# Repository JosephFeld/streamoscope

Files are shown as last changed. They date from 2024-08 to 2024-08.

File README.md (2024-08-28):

# Streamoscope
The Streamoscope is a USB-3 data acquisition system designed for low-field MRI, but could be more generally used. It streams two channels at 60 megasamples per second with 14-bit precision and costs around $300 in parts. It can read in data with low latency and the limit of how much can be read is only limited by the RAM on your computer!

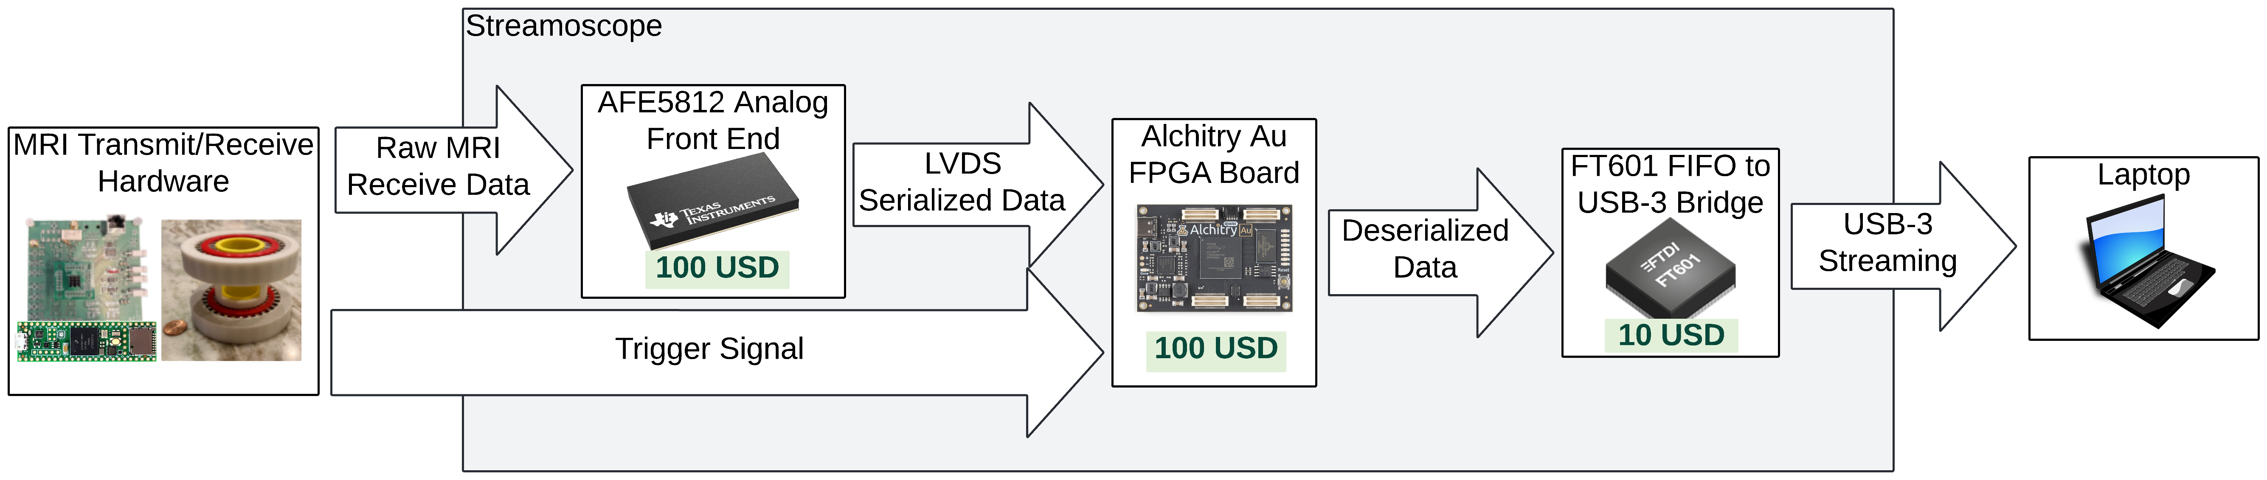
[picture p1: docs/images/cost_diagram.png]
Cost Diagram


It reads in 8 channels of data from the [AFE5812 analog front end chip](https://www.ti.com/product/AFE5812) into an [Alchitry Au FPGA board](https://www.sparkfun.com/products/16527), which feeds it into an [FT601 FIFO-to-USB-3 Bridge](https://ftdichip.com/products/ft601q-b/) which can be read into [Python](https://www.python.org/). Due to bandwidth constraints of the FT601, it only streams two channels. However, more could be streamed with a modified FPGA design that decimates the signals or decreases their precision.

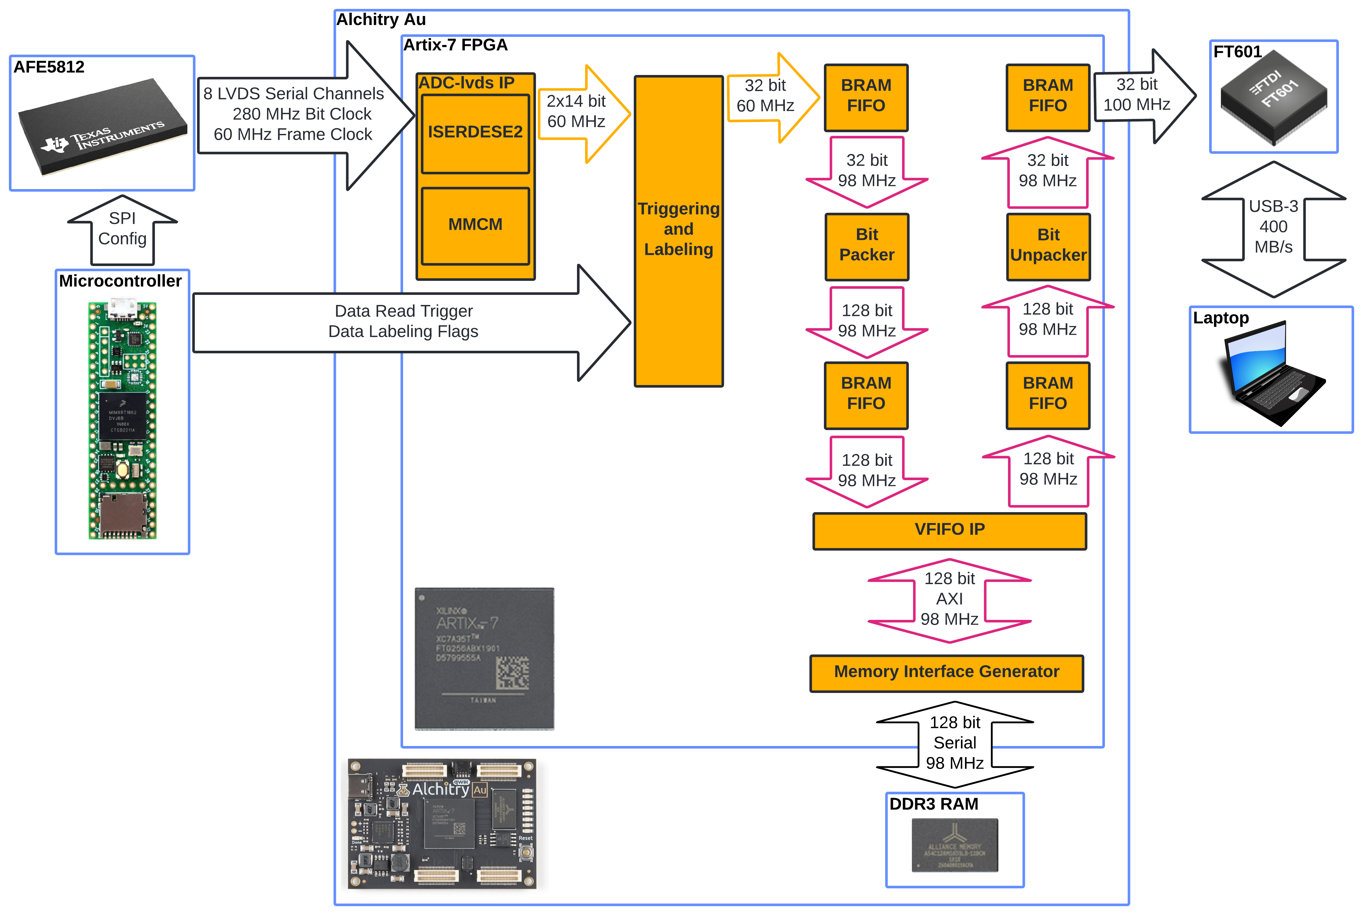
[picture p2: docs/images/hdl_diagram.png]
HDL Diagram


What follows are guides on how to access the various components of the system. To summarize them:

* PCB design files from KiCad
* Python code for reading in data from the FT601
* Teensy code for configuring the AFE5812
* How to configure the Alchitry Au FPGA
* A Vivado project for the FPGA design

# PCB

The PCB design was done in [KiCad 8.0](https://www.kicad.org/) and can be found in ```streamoscope/hardware/kicad_design```. There are custom footprints used, which are accessible in this [library](https://github.com/JosephFeld/Handheld-MRI-Parts). Special thanks to [Lopfi for making the Alchitry Au footprint](https://github.com/Lopfi/alchitry-element-kicad).

# Python Setup

Streamoscope data can be read into Python, and this guide will walk through setting up the Jupyter Notebook example. This uses Python 3, which can be downloaded [here](https://www.python.org/downloads/).

## Installing libusb

First, we need to install [libusb](https://libusb.info/).

### MacOS

On MacOS, run these commands in the terminal: 
```
brew install libusb
sudo ln -s /opt/homebrew/lib/libusb-1.0.0.dylib /usr/local/lib/libusb.dylib
```

### Windows

On Windows, download the latest libusb Windows binaries [here](https://libusb.info/) under Downloads>Latest Windows Binaries.

Unzip the file and choose a version corresponding to your operating system. A good default is the newest Visual Studio folder VS2022. Choose the subfolder corresponding to your operating system, either 32 or 64 for 32-bit or 64-bit systems, respectively. Copy ```libusb-1.0.dll``` in the ```dll``` folder into ```C:/Windows/System32```, which will require admin approval. ```libusb-1.0.dll``` can also be placed into the same directory as the python script, ```streamoscope/software/python_reading``` for this example.

The FT601 on the Streamoscope may have the incorrect drivers. To fix this, install [Zadig](https://zadig.akeo.ie/) and run it.

* Select Options\>List All Devices
* Select FTDI SuperSpeed-FIFO Bridge (Interface 0)
* Use the arrows on the right to select libusbK as the new driver.

Here's what it should look like:
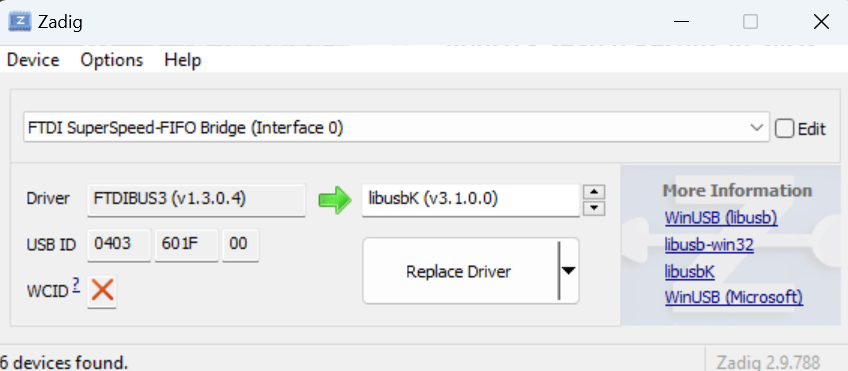
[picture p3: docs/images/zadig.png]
Zadig


* Click "Replace Driver"

## Python dependencies

Then install the Python dependencies

```
pip install libusb, pyusb, matplotlib, numpy, scipy, jupyter
```

## Jupyter Notebook Setup

In the terminal, cd into ```streamoscope/software/python_reading``` and run this command to start up the Jupyter Notebook:

```jupyter notebook .\spin_echo_reader.ipynb```

# Teensy Setup

The Streamoscope uses a Teensy 4.1 microcontroller to configure the AFE5812 Analog Front End and ADC. The software for programming the Teensy can be found [here](https://www.pjrc.com/teensy/td_download.html).

To plug the Teensy into the Streamoscope, connect these pins:

| Streamoscope Pin | Teensy Pin |
| ---------------- | ---------- |
| ADC_RESET        | 3          |      
| MISO             | 39         |
| MOSI             | 26         |
| SCLK             | 27         |
| CS_AFE           | 38         |

And program the Teensy using the code in ```streamoscope\software\teensy_4_1_afe5812_config\teensy_4_1_afe5812_config.ino```. Every time the Teensy powers up, it reconfigures the AFE5812. 

# Configuring Alchitry Au

The Alchitry Au can be programmed using [Alchitry Loader](https://alchitry.com/alchitry-labs/) with the bitstreams found in ```streamoscope/fpga_configurations/```. It is also compatible with [openFPGALoader](https://github.com/trabucayre/openFPGALoader).

There is also a JTAG port broken out which can be used with JTAG programmers like [this](https://digilent.com/shop/jtag-hs3-programming-cable/), which can enable use of the Vivado ILA.

Here are descriptions of each bitstream:

| Filename | Description |
| ---------------- | ---------- |
| teensy_triggered.bit  | Streams channels 1 and 3 with data validity set by GPIO_0 (active high). This is useful for individual spin echoes. |      
| teensy_triggered_with_500ms_trigger_extension.bit | Streams channels 1 and 3 with data validity set by GPIO_0 (active high). Validity lasts an extra 500 milliseconds after GPIO_0 goes low. This is useful for fast imaging sequences. |

# Vivado Project Setup
The FPGA design was made in [Vivado 2023.2](https://www.xilinx.com/support/download/index.html/content/xilinx/en/downloadNav/vivado-design-tools/2023-2.html). It is only necessary to use this if you need to modify the HDL on the FPGA since There is already a provided FPGA configuration.

Open the Vivado GUI, go to the tcl console on the bottom, and cd into the ```streamoscope/hdl/Streamoscope/``` directory. Then run this command:

```
source Streamoscope.tcl
```

Then wait for a bit while the project configures. It will open up the new Streamoscope project. Then in the new project's tcl console, generate the modified ADC LVDS IP with these commands:

```
cd ../ADC-lvds-main/ip
source adc_lvds_ip.tcl
```

Then run this command in the Streamoscope tcl console to update the IP catalog:

```
update_ip_catalog -rebuild
```

If you're running on a version after 2023.2, you may need to update the IP versions. You can do that by navigating to Reports>Report IP Status. In the menu that pops up, select Upgrade Selected.

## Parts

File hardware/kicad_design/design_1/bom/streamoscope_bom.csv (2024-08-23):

Id | Designator | Footprint | Quantity | Designation | Supplier and ref | supplemental parts
1 | J7 | PinHeader_1x32_P2.54mm_Vertical | 1 | Conn_01x32_Pin | https://www.mouser.com/ProductDetail/TE-Connectivity/3-826936-2?qs=xF5SkmKSM76zfahaczRa9A%3D%3D
2 | F1 | Fuse_0402_1005Metric_Pad0.77x0.64mm_HandSolder | 1 | Fuse | https://www.mouser.com/ProductDetail/Littelfuse/043502.5KRHF?qs=PalBzRKzfnviFVYPMWoZ5g%3D%3D
3 | J16 | PinHeader_1x16_P2.54mm_Vertical | 1 | Conn_01x16_Pin | https://www.mouser.com/ProductDetail/Amphenol-FCI/68024-116HLF?qs=C9AXj6SgtYUh%2FNWF9cqh4A%3D%3D | https://www.mouser.com/ProductDetail/Samtec/IDSS-16-D-20.00?qs=rU5fayqh%252BE0O0Dd9%252BPEI9Q%3D%3D
4 | J15 | AMPHENOL_12401899E412A | 1 | USB_C_Receptacle | https://www.mouser.com/ProductDetail/Amphenol-Commercial-Products/12401899E412A?qs=0lSvoLzn4L%2FxruERFi%2FtTg%3D%3D
5 | C33,C31,C17,C16,C42,C29,C30,C44,C32,C55,C43 | C_0402_1005Metric_Pad0.74x0.62mm_HandSolder | 11 | 1u | https://www.mouser.com/ProductDetail/KYOCERA-AVX/KGM05AR51A105KH
6 | R7,R8,R10,R15 | R_0402_1005Metric_Pad0.72x0.64mm_HandSolder | 4 | 10k | https://www.mouser.com/ProductDetail/TE-Connectivity-Holsworthy/RN73C1E10KBTD?qs=CXI0wBT1M2iAWhqqLC6L1g%3D%3D
7 | C9,C35,C10,C11,C34,C12,C5,C13 | C_0402_1005Metric_Pad0.74x0.62mm_HandSolder | 8 | 15n | https://www.mouser.com/ProductDetail/KEMET/C0402C153K3RACTU?qs=ZP3UR5XsUoduxSHfolMWsA%3D%3D
8 | C38,C15,C47,C53,C20,C23,C78,C3,C40,C50,C58,C19,C41,C26,C45,C51,C79,C46,C27,C14,C39,C36,C77,C28,C24,C25,C57,C22,C4,C48,C21,C49,C18,C37,C56 | C_0402_1005Metric_Pad0.74x0.62mm_HandSolder | 35 | 0.1u | https://www.mouser.com/ProductDetail/KYOCERA-AVX/0402X7R104KT7AT
9 | J1 | PinHeader_1x02_P2.54mm_Vertical | 1 | Conn_01x02_Pin
10 | C7,C2,C8,C1 | CP_EIA-6032-20_AVX-F | 4 | 22u | https://www.mouser.com/ProductDetail/KYOCERA-AVX/TPSC226K016R0375?qs=iBwFsHVUAOd%252BY4clhItAJQ%3D%3D
11 | FB3,FB7,FB5,FB9,FB8,FB6,FB2,FB4 | L_0805_2012Metric | 8 | FerriteBead | https://www.mouser.com/ProductDetail/Laird-Performance-Materials/HI0805R800R-10?qs=UV0HhPl4yOF%252BhNGXb8sElA%3D%3D
12 | J11,J8,J13,J6,J10,J9,J5,J12 | SMA_Amphenol_132134_Vertical | 8 | Conn_Coaxial | https://www.mouser.com/ProductDetail/LPRS/SMA-CONNECTOR?qs=j%252B1pi9TdxUYkOiITvzJM8A%3D%3D
13 | FB11 | L_0402_1005Metric | 1 | FerriteBead | https://www.mouser.com/ProductDetail/Murata-Electronics/BLM15BD102SN1D?qs=VC7md5PxyA1Y4EgP9YhX%252BA%3D%3D
14 | C59,C61,C72,C54,C62,C63,C68,C66,C67 | C_0402_1005Metric_Pad0.74x0.62mm_HandSolder | 9 | 100n | https://www.mouser.com/ProductDetail/KYOCERA-AVX/0402X7R104KT7AT
15 | JPG1,JPG2 | R_0402_1005Metric_Pad0.72x0.64mm_HandSolder | 2 | 0 | https://www.mouser.com/ProductDetail/Vishay-Dale/CRCW04020000Z0EDC?qs=sGAEpiMZZMtlubZbdhIBIIZe04wfiaJW9KIkhfRMZVI%3D
16 | C73,C70,C71,C69,C65,C64 | C_0402_1005Metric_Pad0.74x0.62mm_HandSolder | 6 | 470n | https://www.mouser.com/ProductDetail/KYOCERA-AVX/0402ZC474KAT2A
17 | R1 | R_0402_1005Metric_Pad0.72x0.64mm_HandSolder | 1 | 49.9 | https://www.mouser.com/ProductDetail/Panasonic/ERA-2AED49R9X?qs=sGAEpiMZZMtlubZbdhIBIKHZJwodQ036pHeX4trellw%3D
18 | D2,D1 | LED_0603_1608Metric | 2 | Green | https://www.mouser.com/ProductDetail/ROHM-Semiconductor/SMLD12EN1WT86?qs=qSfuJ%252Bfl%2Fd4fR%252B9yZydIwg%3D%3D
19 | R3,R2 | R_0402_1005Metric_Pad0.72x0.64mm_HandSolder | 2 | 200 | https://www.mouser.com/ProductDetail/Vishay-Dale/CRCW0402200RFKEDHP?qs=sGAEpiMZZMtlubZbdhIBIHEwn6Ulz00PjH77PBDsIyo%3D
20 | X1 | Oscillator_SMD_Abracon_ASV-4Pin_7.0x5.1mm | 1 | XO32 | https://www.mouser.com/ProductDetail/ABRACON/ASV-60.000MHZ-E-T?qs=NE97hfUNX0FMmM33%252BKetqA%3D%3D&countryCode=US&currencyCode=USD
21 | U1 | IC_TPS61196PWPRQ1 | 1 | TPS767D318PWPR | https://www.mouser.com/ProductDetail/Texas-Instruments/TPS767D318PWPR?qs=6zVL%252ByCp0mo1sIrGyoyUVQ%3D%3D
22 | J14 | BarrelJack_Horizontal | 1 | Barrel_Jack | https://www.mouser.com/ProductDetail/Wurth-Elektronik/694106301002?qs=a9WhcLg8qCwOEkcI62k5mA%3D%3D | alt: | https://www.digikey.com/en/products/detail/cui-devices/PJ-002AH/408446
23 | IC1 | SOT95P280X130-5N | 1 | MIC7221YM5-TR | https://www.mouser.com/ProductDetail/Microchip-Technology/MIC7221YM5-TR?qs=U6T8BxXiZAWrxxu6IxkTvA%3D%3D
24 | C52,C60 | C_0402_1005Metric_Pad0.74x0.62mm_HandSolder | 2 | 6.8n | https://www.mouser.com/ProductDetail/KYOCERA-AVX/04025C682K4T2A
25 | U2 | QFN40P900X900X100-77N | 1 | FT601Q-B-T | https://www.mouser.com/ProductDetail/FTDI/FT601Q-B-T?qs=p9T7GgSe1IHuZCV7KGuelQ%3D%3D
26 | U4 | ZCF135_TEX_NO_PASTE | 1 | AFE5812ZCF | https://www.mouser.com/ProductDetail/Texas-Instruments/AFE5812ZCF?qs=jpHf3Ogds1wdWEifNjYuZA%3D%3D
27 | R4,R5 | R_0402_1005Metric_Pad0.72x0.64mm_HandSolder | 2 | 250K | https://www.mouser.com/ProductDetail/Panasonic/ERJ-PA2D2493X?qs=sGAEpiMZZMtlubZbdhIBIA9n2NI7aX0AgwM9v08p8RI%3D
28 | R12,R6 | R_0402_1005Metric_Pad0.72x0.64mm_HandSolder | 2 | 5.1k | https://www.mouser.com/ProductDetail/Vishay-Dale/CRCW04025K10JNED
29 | J3 | PinSocket_2x07_P2.00mm_Vertical | 1 | Conn_02x07_Odd_Even | https://www.mouser.com/ProductDetail/Molex/87831-1435?qs=kNSQ05%252BLZoDWRPEqPkM6DQ%3D%3D
30 | R16,R14 | R_0402_1005Metric_Pad0.72x0.64mm_HandSolder | 2 | 100k | https://www.mouser.com/ProductDetail/Panasonic/ERJ-H2RD1003X?qs=eP2BKZSCXI4AgmLrPoTcjA%3D%3D
31 | U3 | SN74HCS541RKSR | 1 | HD3SS3212IRKSR | https://www.mouser.com/ProductDetail/Texas-Instruments/HD3SS3212IRKSR?qs=GURawfaeGuCBk5SYUlUAfw%3D%3D
32 | C75,C74 | C_0402_1005Metric_Pad0.74x0.62mm_HandSolder | 2 | 18p | https://www.mouser.com/ProductDetail/KYOCERA-AVX/04025A180GAT2A?qs=tGdZP2ZdRP0kqZUhomJhdQ%3D%3D
33 | C6 | C_0402_1005Metric_Pad0.74x0.62mm_HandSolder | 1 | 0.1u | https://www.mouser.com/ProductDetail/KYOCERA-AVX/0402X7R104KT7AT
34 | C76 | C_0402_1005Metric_Pad0.74x0.62mm_HandSolder | 1 | 10u | https://www.mouser.com/ProductDetail/KYOCERA-AVX/04024D106MAT2A?qs=NBFAU1oqP4W0zKsr62mI7A%3D%3D
35 | R9,R13 | R_0402_1005Metric_Pad0.72x0.64mm_HandSolder | 2 | 4.3k | https://www.mouser.com/ProductDetail/Vishay-Dale/CRCW04024K30JNED?qs=hAuyw6LW%252BLgIGQh4eckejg%3D%3D
36 | R11 | R_0402_1005Metric_Pad0.72x0.64mm_HandSolder | 1 | 1.6k | https://www.mouser.com/ProductDetail/Vishay-Dale/CRCW04021K60FKTD?qs=8YOjkUvjcV0g3cR%252BZ1c%2FJA%3D%3D
37 | Y1 | Crystal_SMD_3225-4Pin_3.2x2.5mm | 1 | 30Meg | https://www.mouser.com/ProductDetail/Wurth-Elektronik/830059646?qs=2WXlatMagcF%252BLmGDoXCbKA%3D%3D
38 | J4 | PinSocket_1x04_P2.54mm_Vertical | 1 | Conn_01x04_Pin | https://www.mouser.com/ProductDetail/Amphenol-FCI/68000-204HLF?qs=osVJq4lsVJeuKNYS29q3NQ%3D%3D
39 | B1 | Element_no_top | 1 | Alchitry_Element_AU | https://www.mouser.com/ProductDetail/SparkFun/DEV-16527?qs=W%2FMpXkg%252BdQ6G3CPW%2FClVVA%3D%3D
40 | TP3 | TestPoint_Pad_2.0x2.0mm | 1 | 3.3VA
41 | TP6 | TestPoint_Pad_2.0x2.0mm | 1 | 1.8VD
42 | TP7 | TestPoint_Pad_2.0x2.0mm | 1 | GND
43 | TP4 | TestPoint_Pad_2.0x2.0mm | 1 | 3.3VD
44 | TP5 | TestPoint_Pad_2.0x2.0mm | 1 | 1.8VA
45 | TP1 | TestPoint_Pad_2.0x2.0mm | 1 | 5VA
46 | TP2 | TestPoint_Pad_2.0x2.0mm | 1 | 5V

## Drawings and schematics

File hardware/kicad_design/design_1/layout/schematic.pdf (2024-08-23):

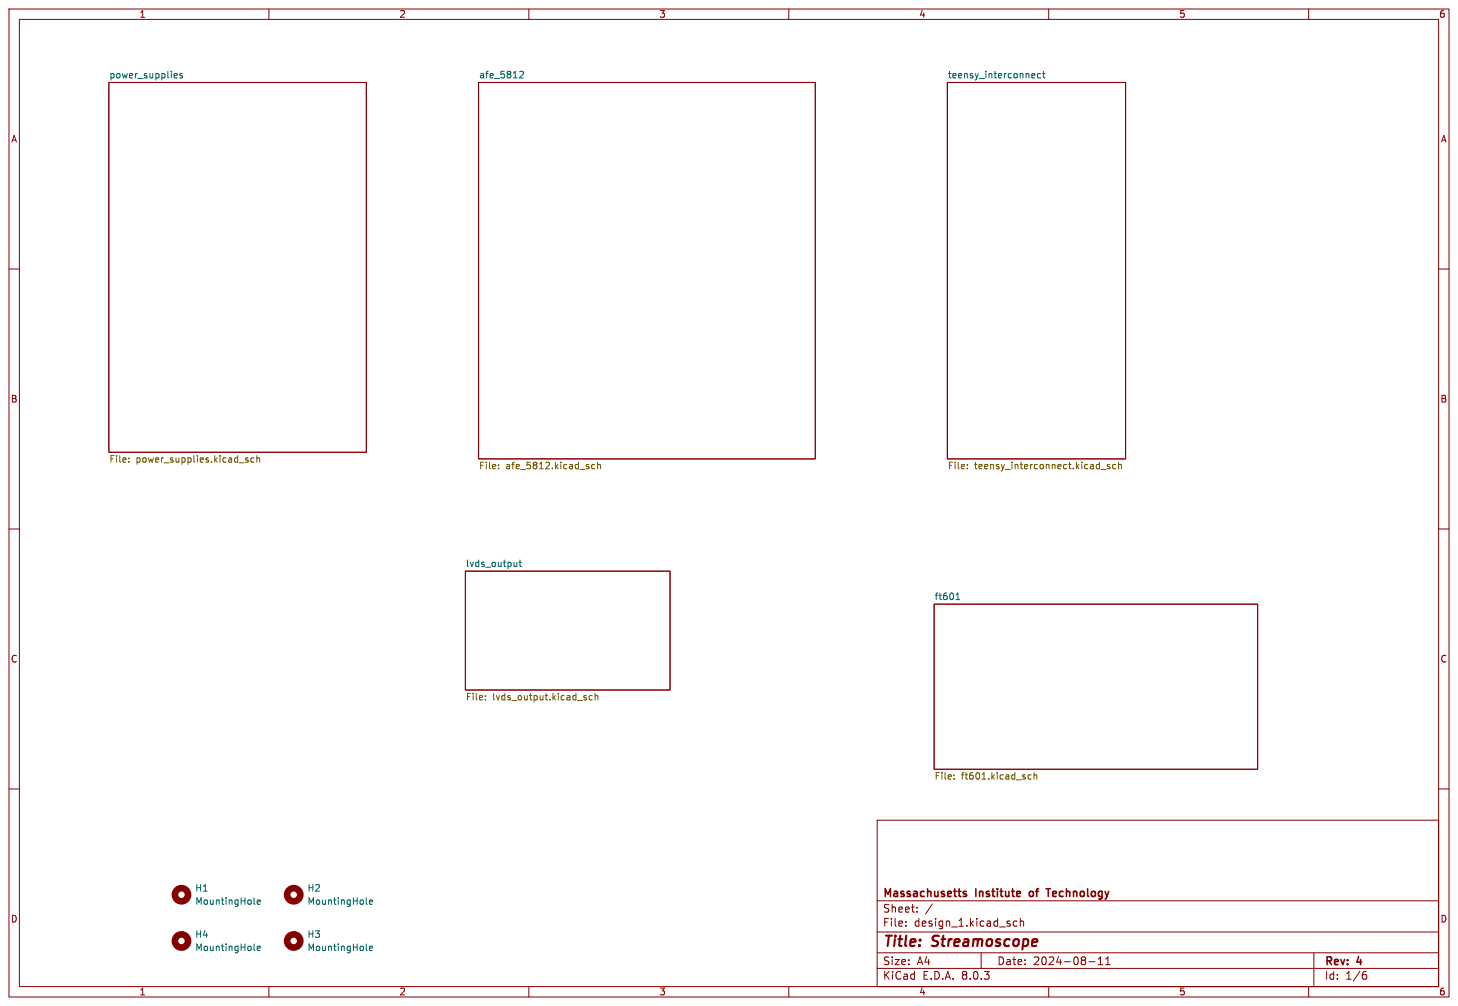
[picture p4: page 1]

ft601 File: ft601.kicad_sch H3 MountingHole H2 MountingHole H4 MountingHole H1 MountingHole

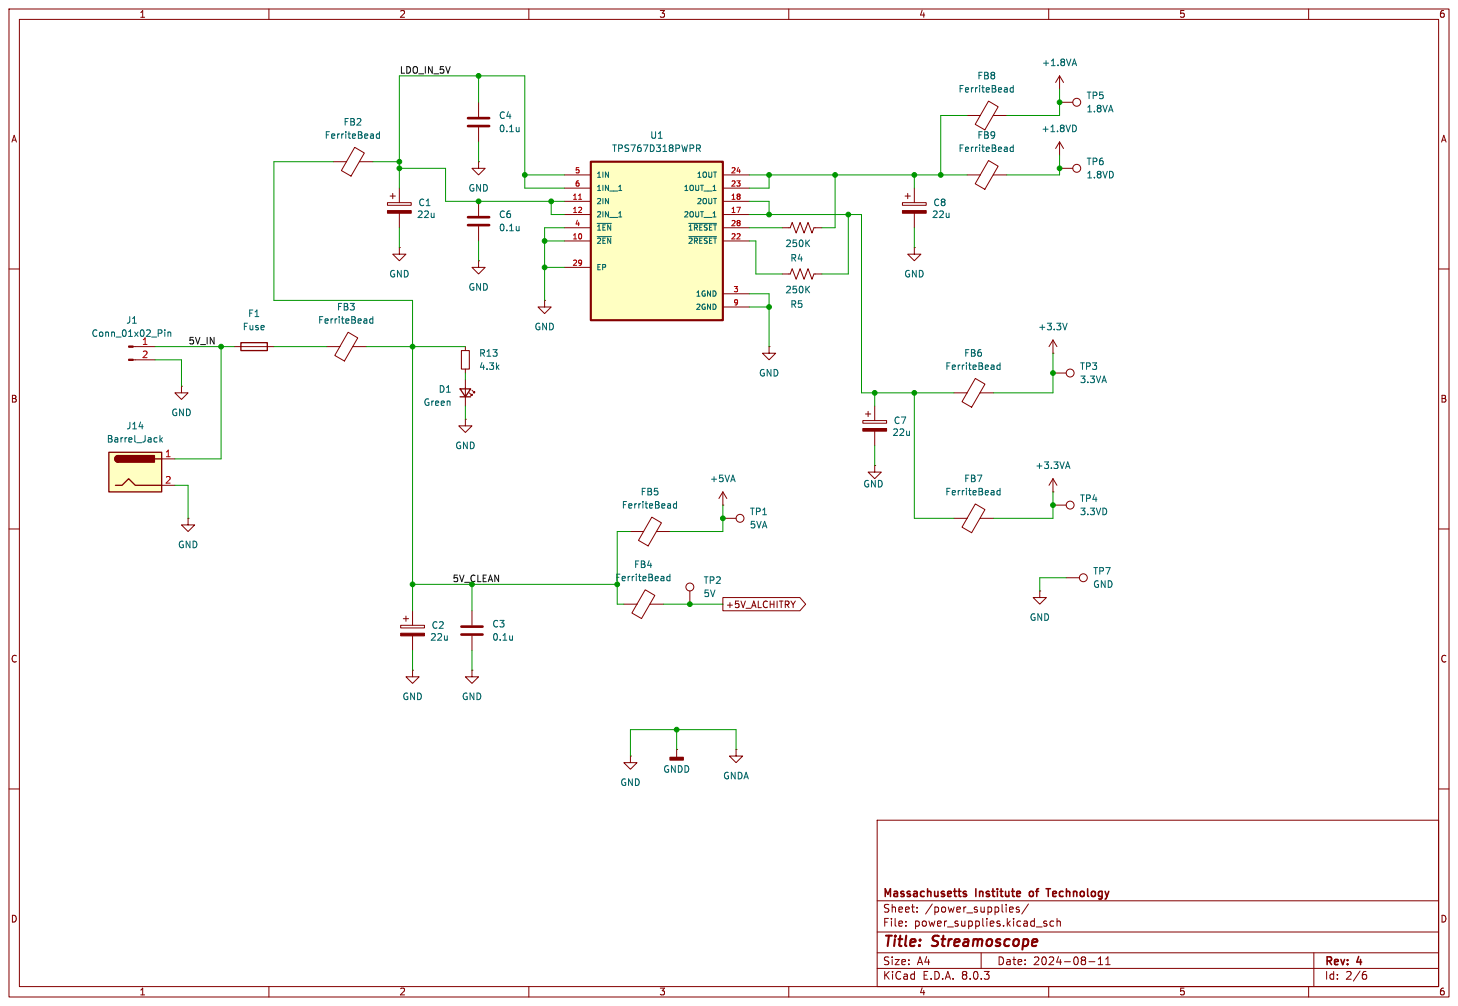
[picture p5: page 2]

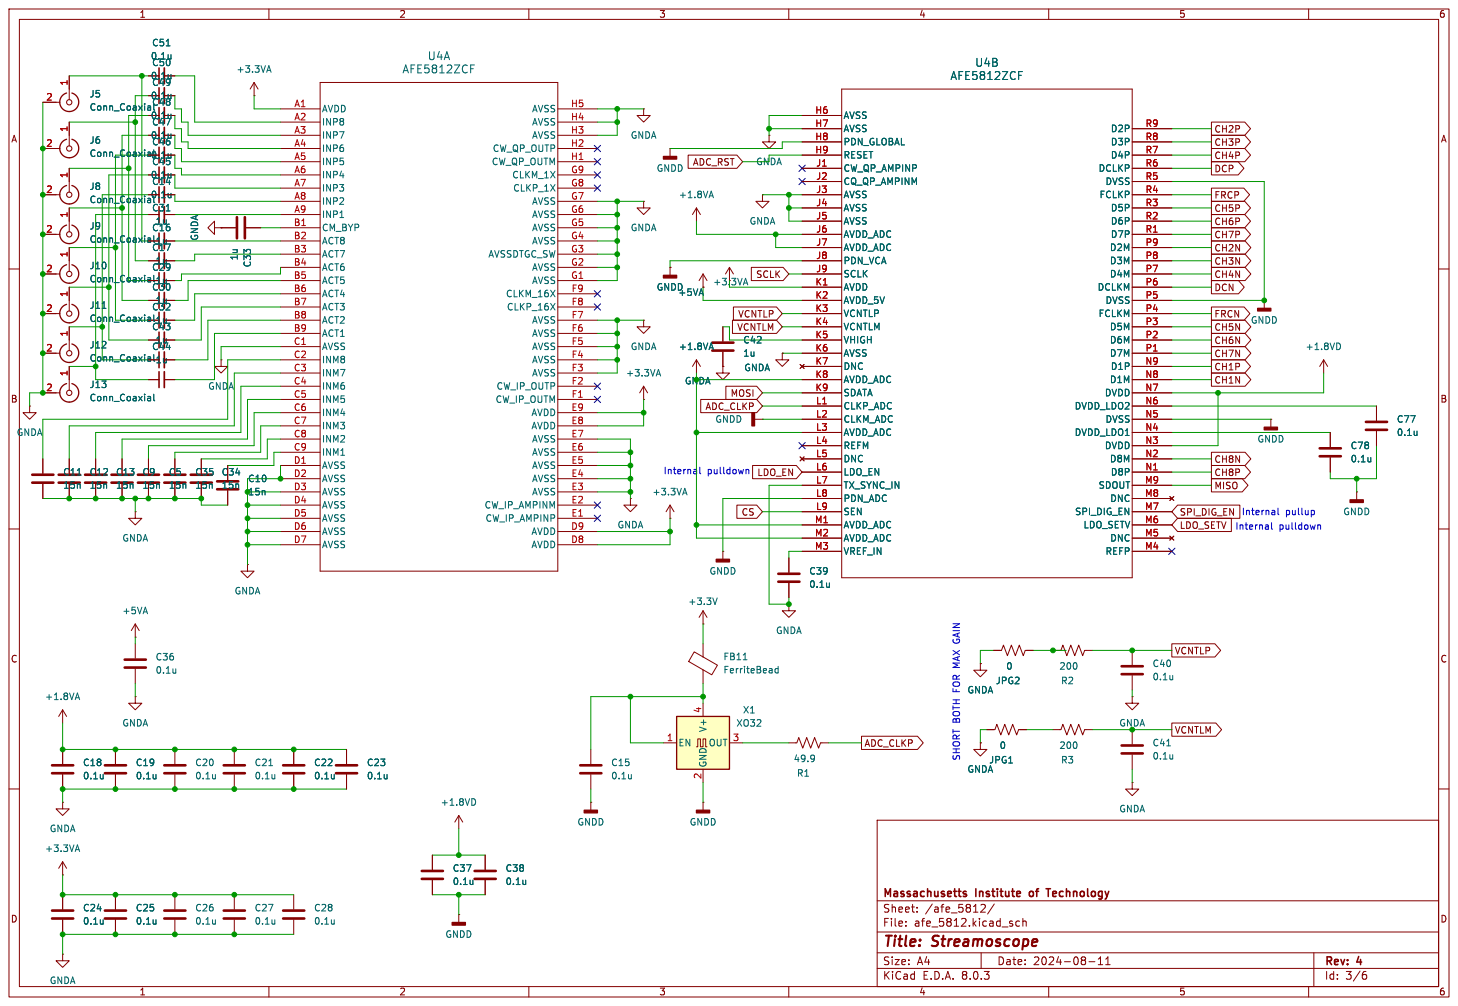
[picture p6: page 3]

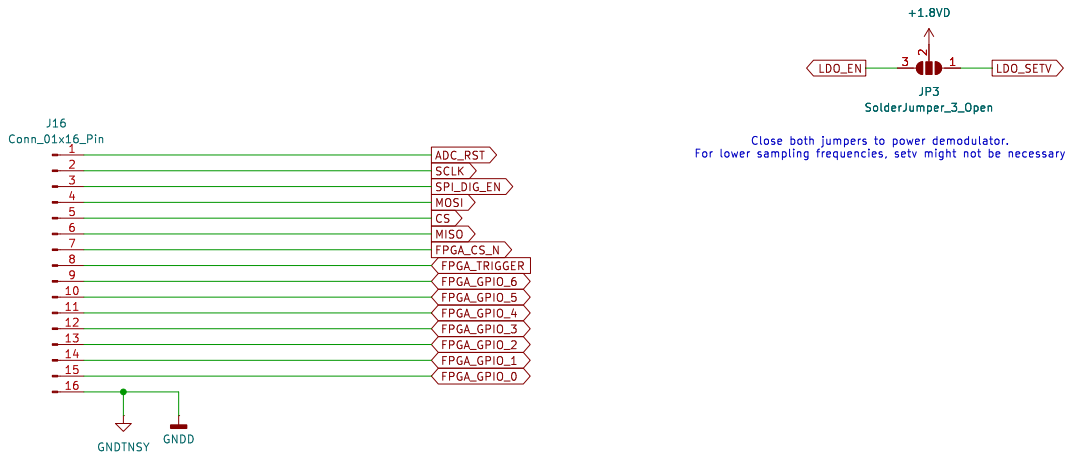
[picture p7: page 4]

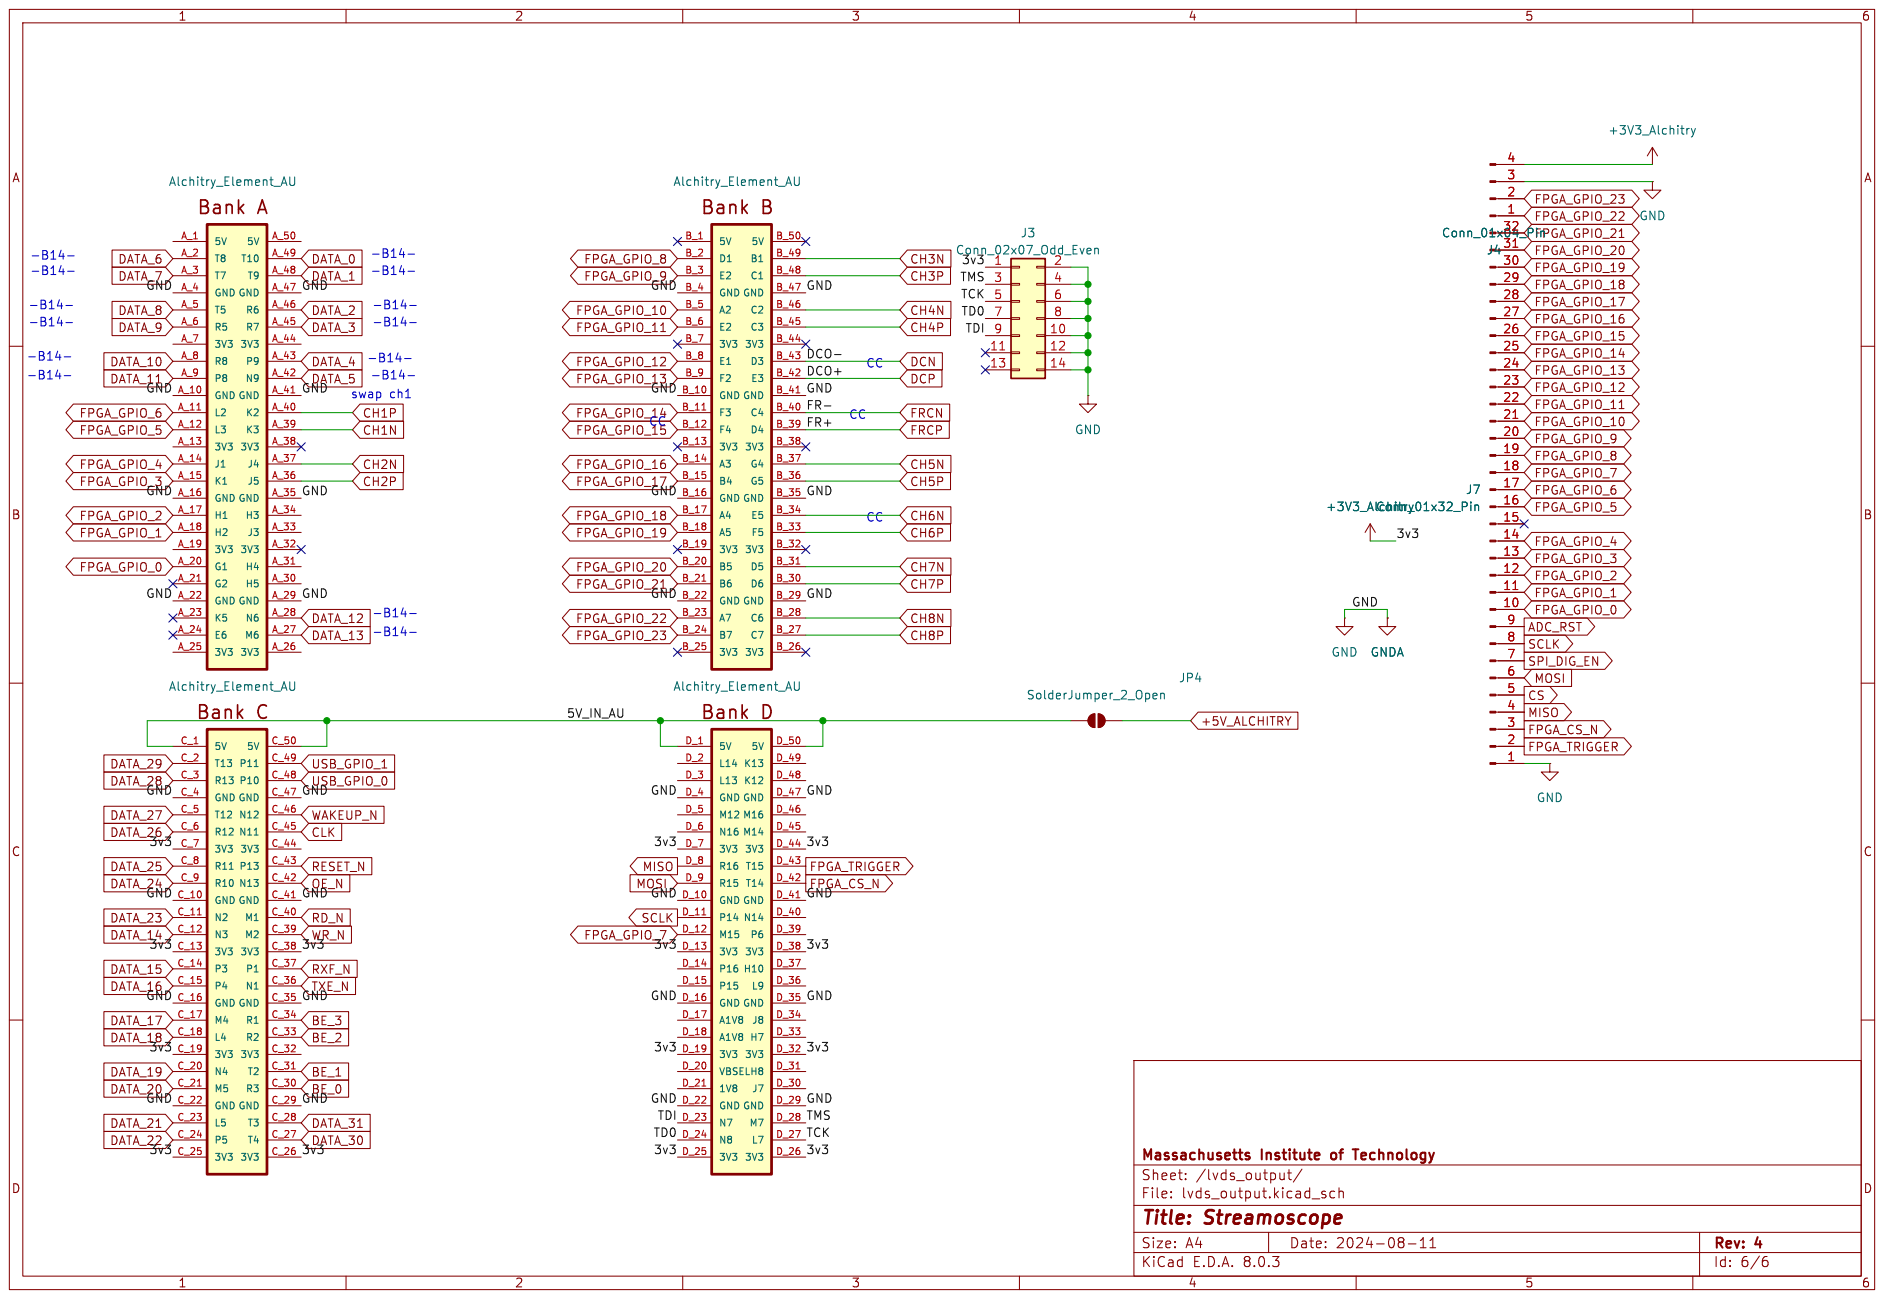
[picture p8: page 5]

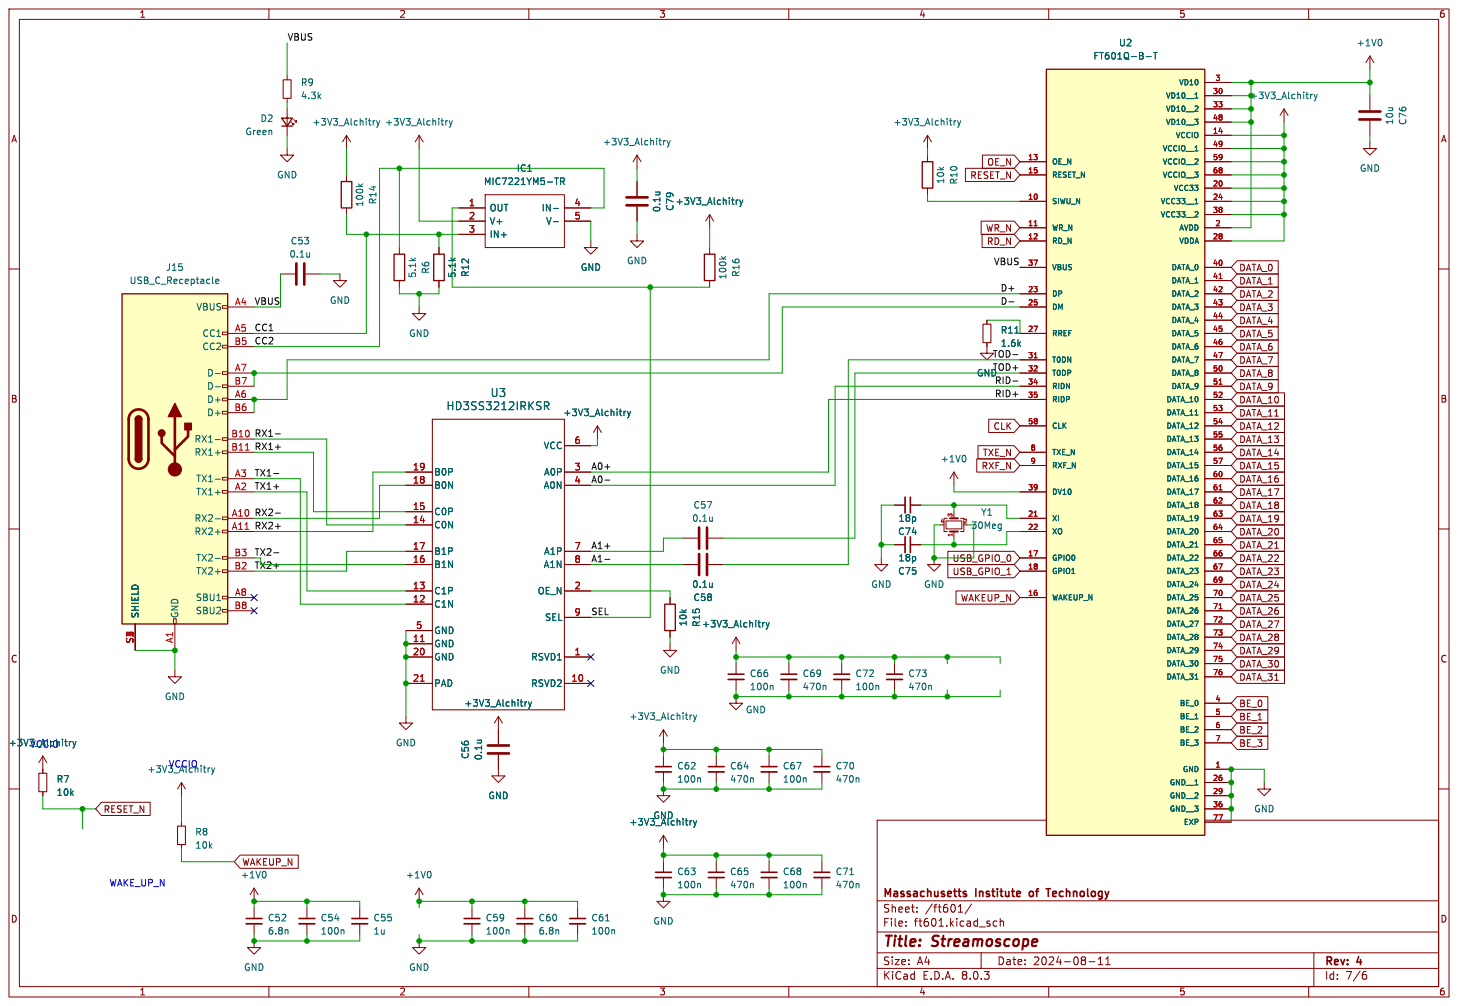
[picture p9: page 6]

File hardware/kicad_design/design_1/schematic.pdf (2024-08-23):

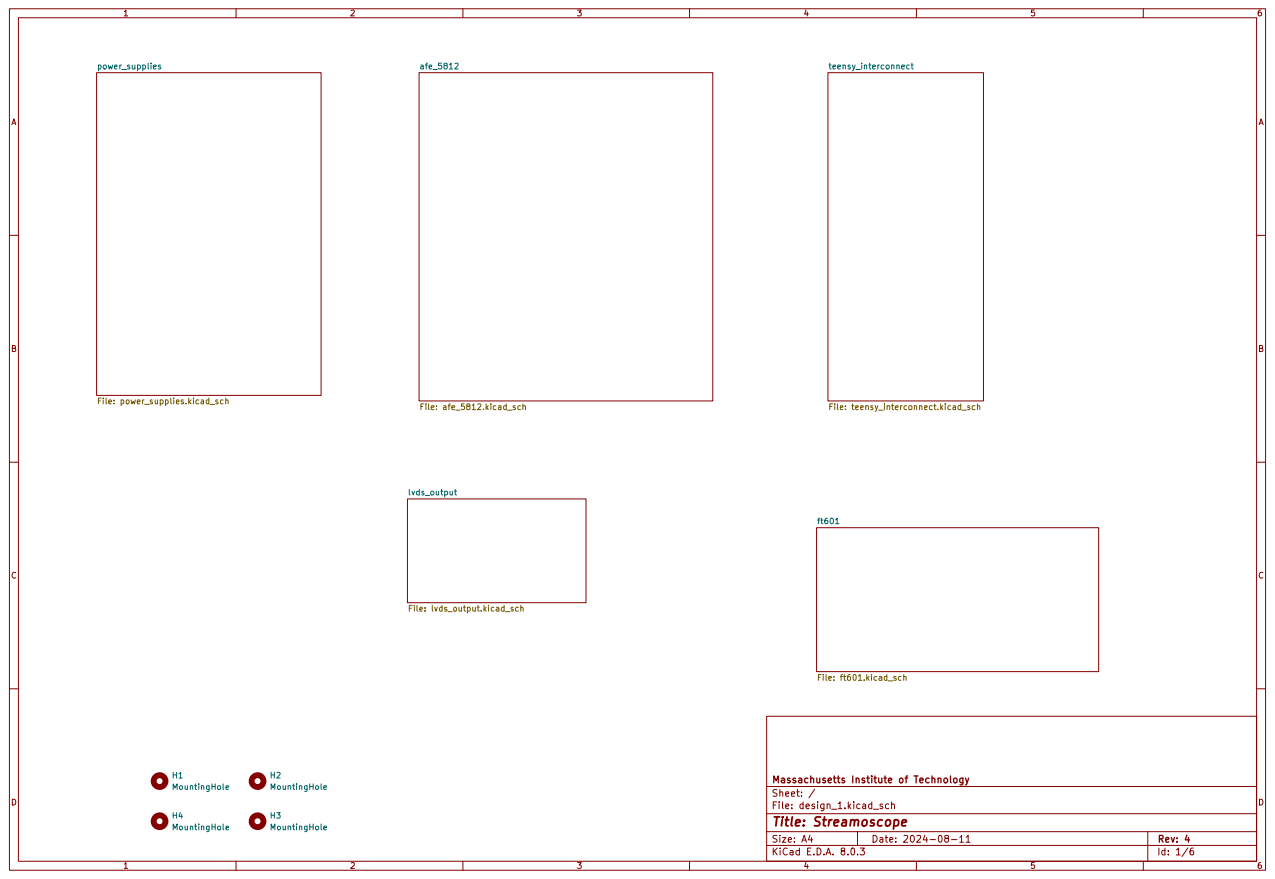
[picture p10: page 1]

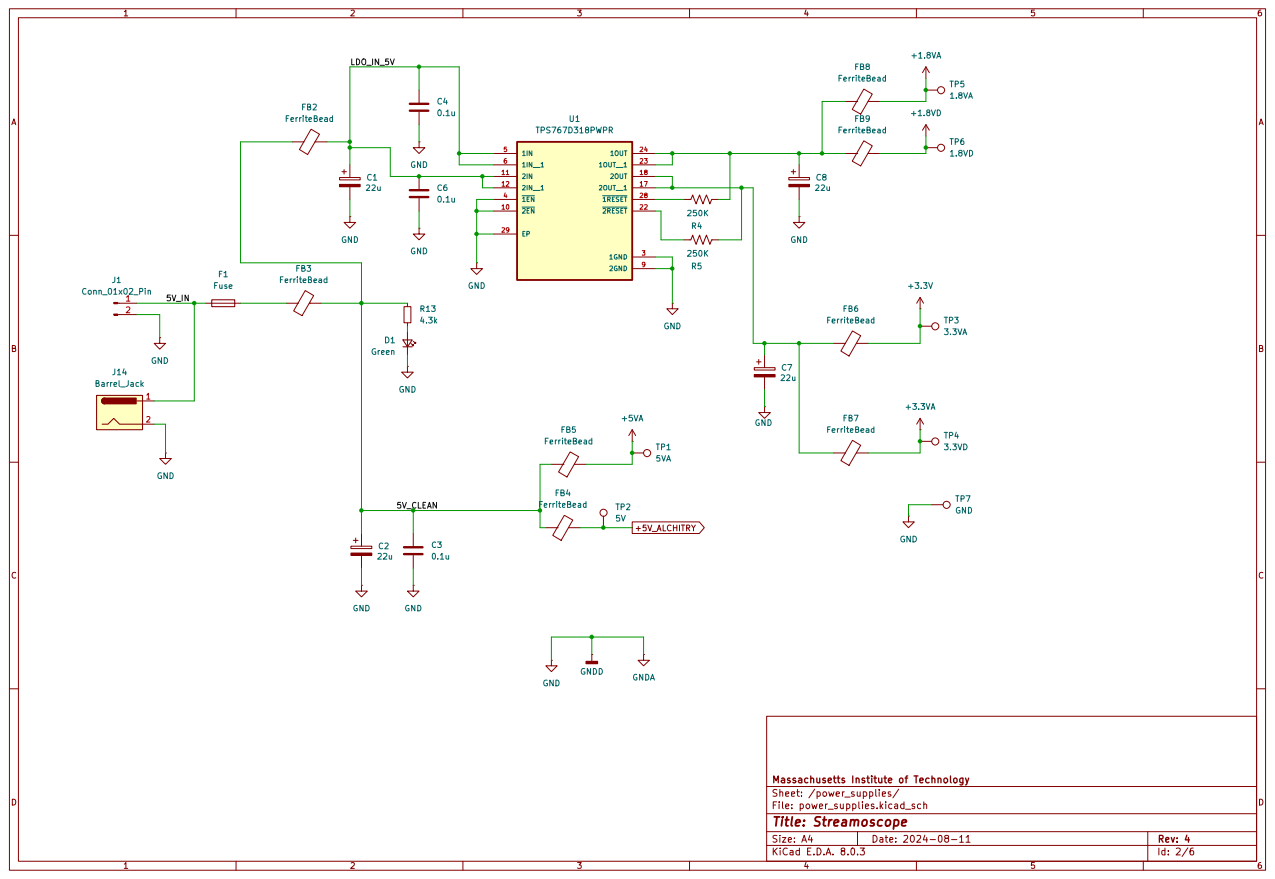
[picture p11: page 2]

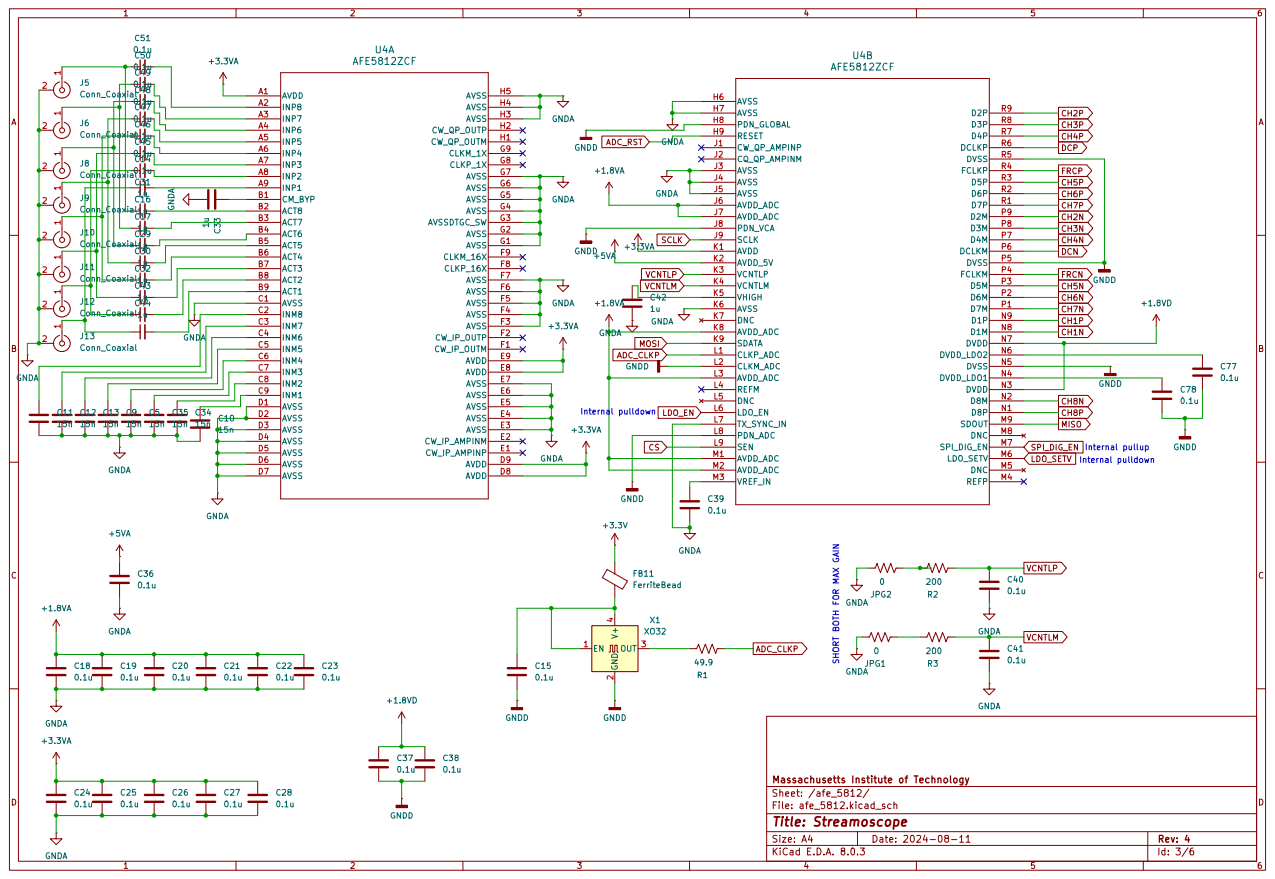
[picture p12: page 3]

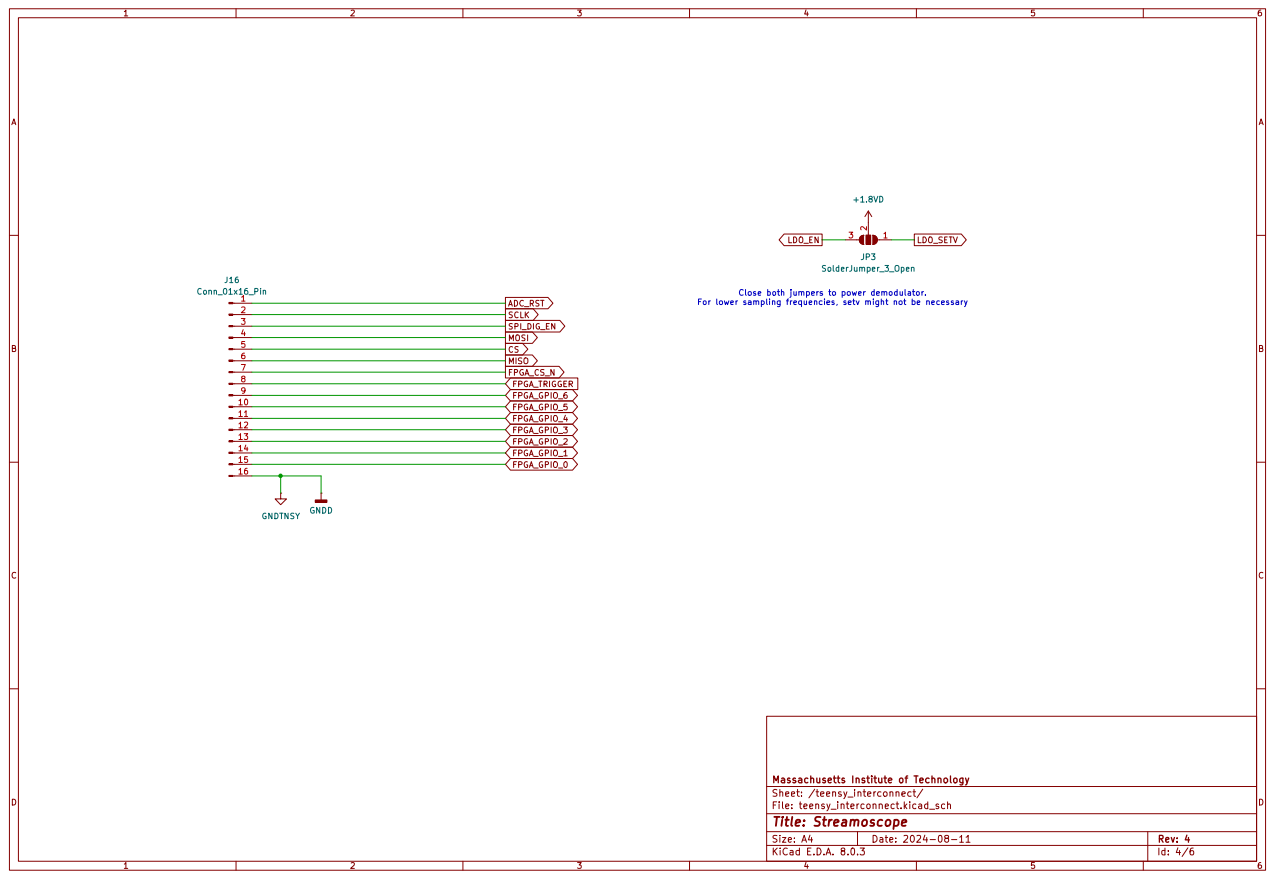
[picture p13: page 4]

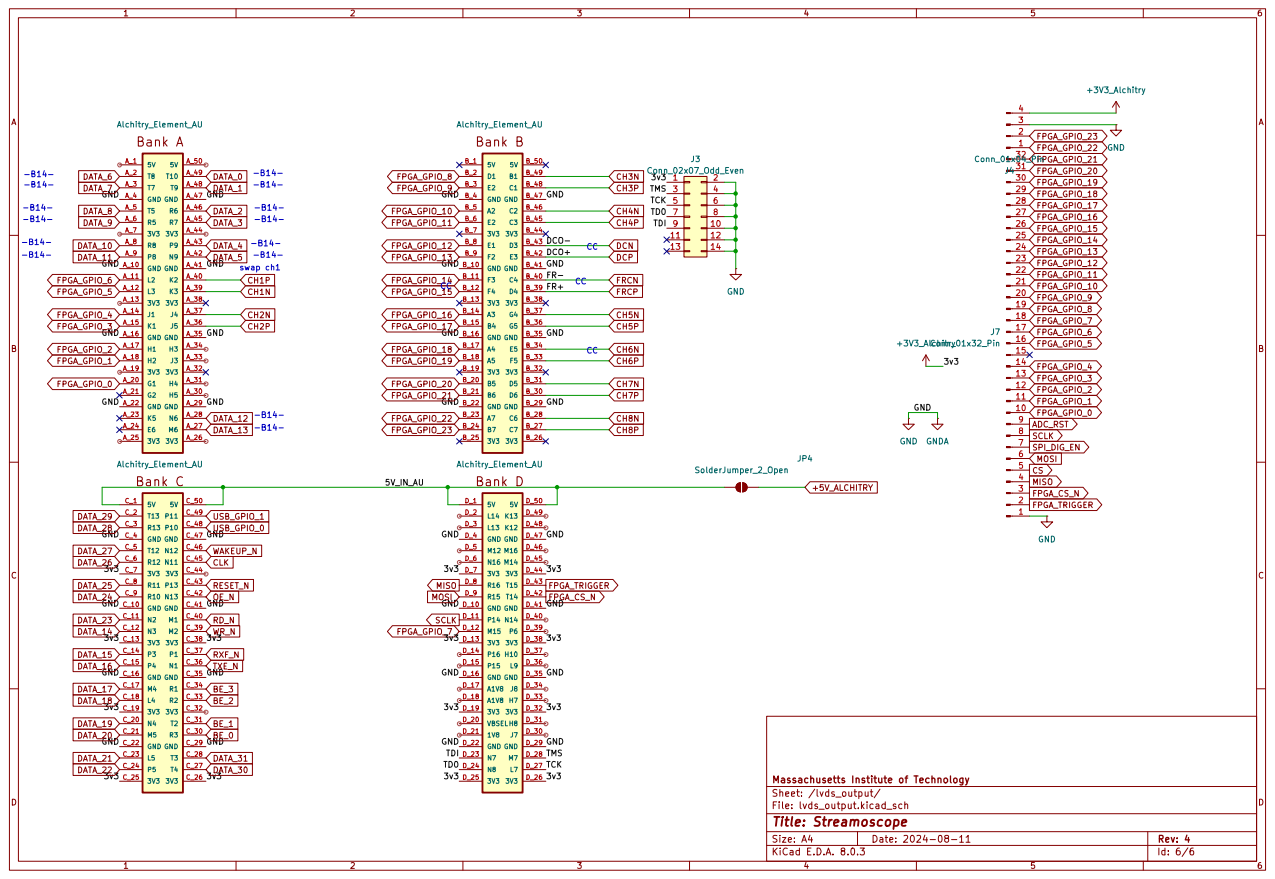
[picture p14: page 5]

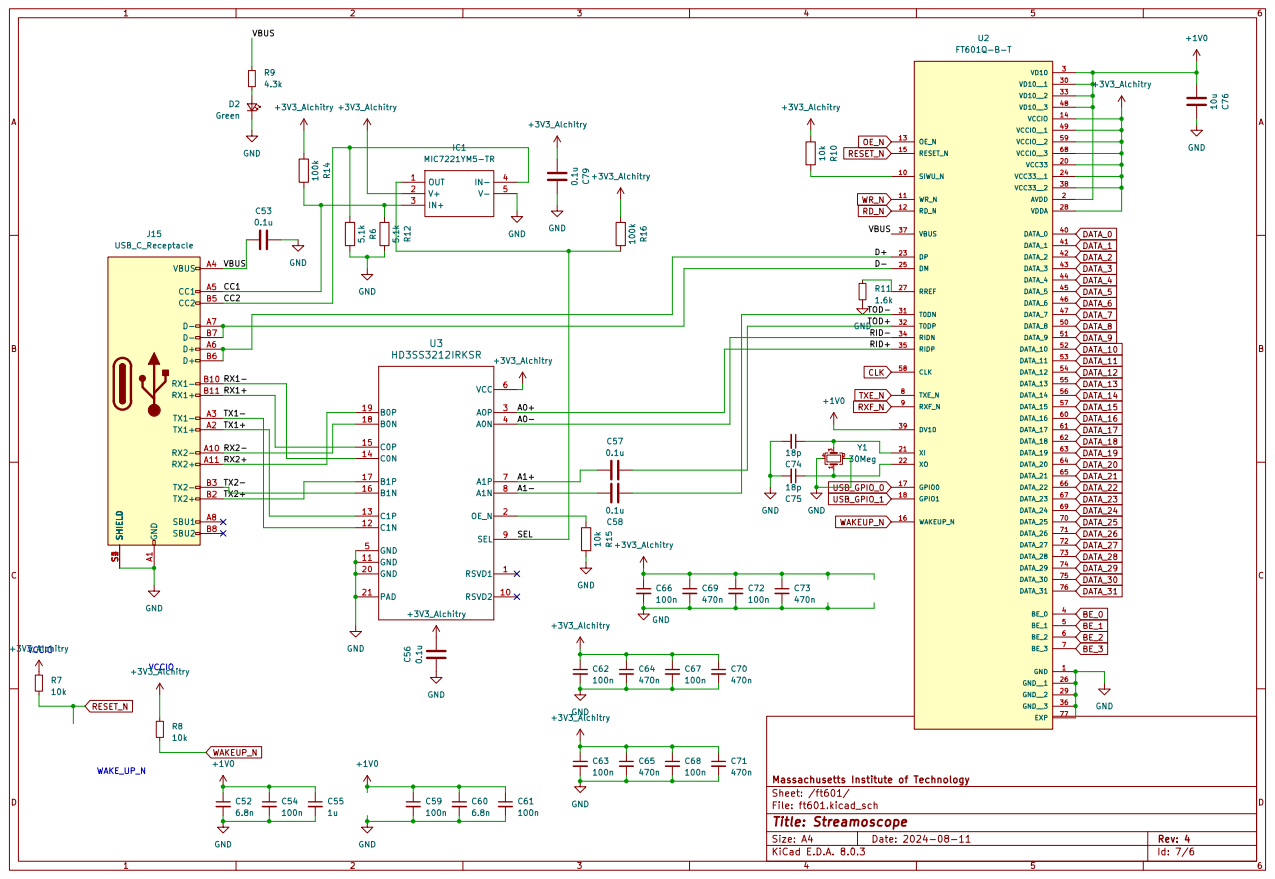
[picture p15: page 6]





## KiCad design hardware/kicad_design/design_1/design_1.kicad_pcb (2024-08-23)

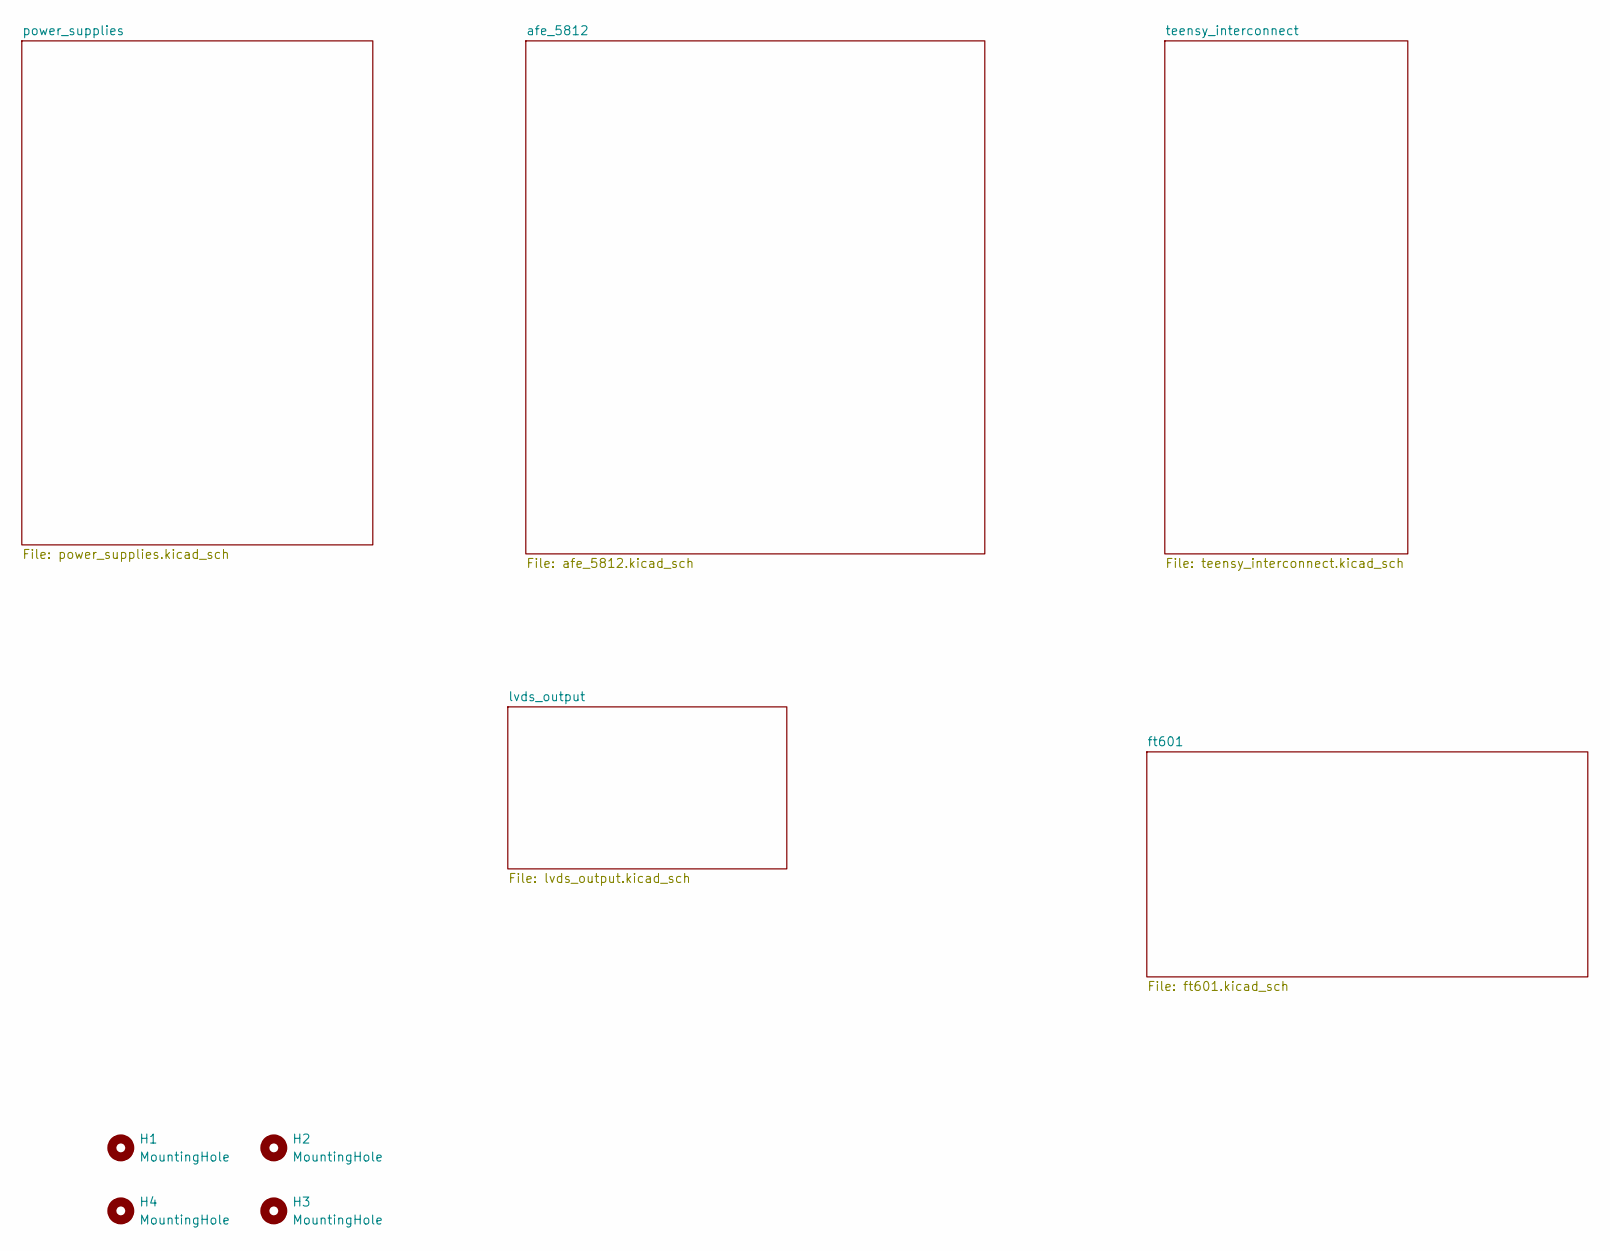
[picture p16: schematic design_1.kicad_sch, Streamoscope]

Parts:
H1, H2, H3, H4: MountingHole; MountingHole_2.2mm_M2

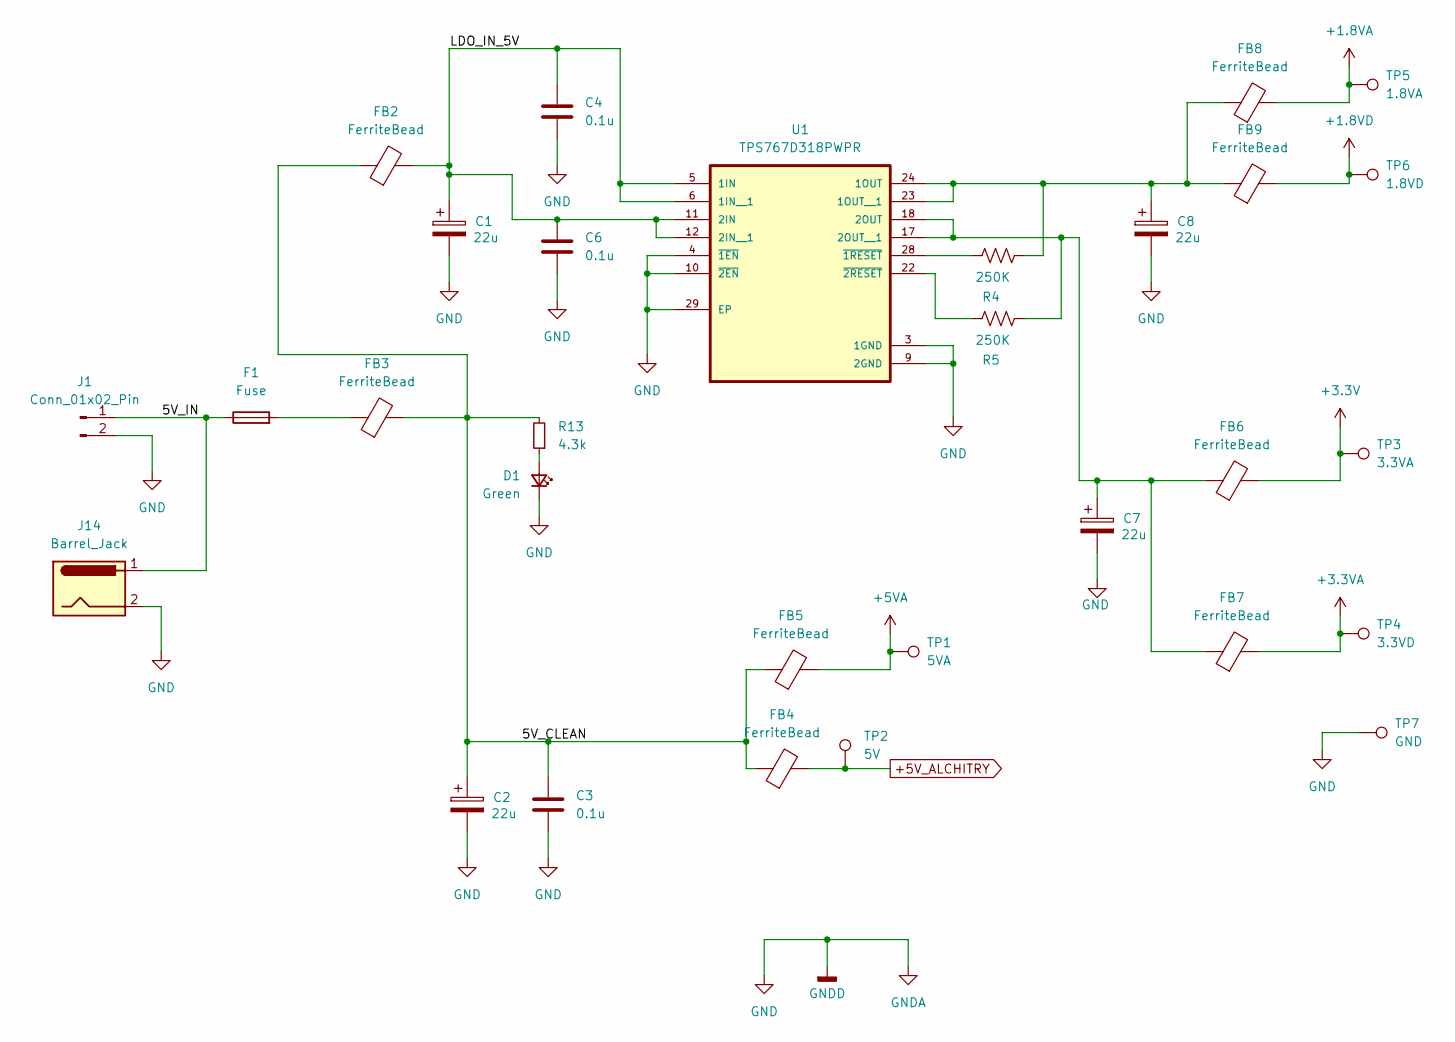
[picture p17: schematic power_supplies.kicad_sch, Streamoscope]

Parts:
C1, C2, C7, C8: 22u; CP_EIA-6032-20_AVX-F
C3, C4, C6: 0.1u; C_0402_1005Metric_Pad0.74x0.62mm_HandSolder
D1: Green; LED_0603_1608Metric
F1: Fuse; Fuse_0402_1005Metric_Pad0.77x0.64mm_HandSolder
FB2, FB3, FB4, FB5, FB6, FB7, FB8, FB9: FerriteBead; L_0805_2012Metric
J1: Conn_01x02_Pin; PinHeader_1x02_P2.54mm_Vertical
J14: Barrel_Jack; BarrelJack_Horizontal
R4, R5: 250K; R_0402_1005Metric_Pad0.72x0.64mm_HandSolder
R13: 4.3k; R_0402_1005Metric_Pad0.72x0.64mm_HandSolder
TP1: 5VA; TestPoint_Pad_2.0x2.0mm
TP2: 5V; TestPoint_Pad_2.0x2.0mm
TP3: 3.3VA; TestPoint_Pad_2.0x2.0mm
TP4: 3.3VD; TestPoint_Pad_2.0x2.0mm
TP5: 1.8VA; TestPoint_Pad_2.0x2.0mm
TP6: 1.8VD; TestPoint_Pad_2.0x2.0mm
TP7: GND; TestPoint_Pad_2.0x2.0mm
U1: TPS767D318PWPR; IC_TPS61196PWPRQ1

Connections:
+1.8VA: FB8.2, TP5.1; also elsewhere on the board
+1.8VD: FB9.2, TP6.1; also elsewhere on the board
+3.3V: FB6.2, TP3.1; also elsewhere on the board
+3.3VA: FB7.2, TP4.1; also elsewhere on the board
+5VA: FB5.2, TP1.1; also elsewhere on the board
+5V_ALCHITRY: FB4.2, TP2.1; also elsewhere on the board
/power_supplies/5V_CLEAN: C2.1, C3.1, FB2.1, FB3.2, FB4.1, FB5.1, R13.2
/power_supplies/5V_IN: F1.1, J1.1, J14.1
/power_supplies/LDO_IN_5V: C1.1, C4.1, C6.1, FB2.2, U1.5 (1IN), U1.6 (1IN__1), U1.11 (2IN), U1.12 (2IN__1)
GND: C1.2, C2.2, C3.2, C4.2, C6.2, C7.2, C8.2, D1.1 (K), J1.2, J14.2, TP7.1, U1.3 (1GND), U1.4 (~1EN), U1.9 (2GND), U1.10 (~2EN), U1.29 (EP); also elsewhere on the board
unnamed: D1.2 (A), R13.1
unnamed: F1.2, FB3.1
unnamed: C8.1, FB8.1, FB9.1, R4.2, U1.23 (1OUT__1), U1.24 (1OUT)
unnamed: C7.1, FB6.1, FB7.1, R5.2, U1.17 (2OUT__1), U1.18 (2OUT)
unnamed: R4.1, U1.28 (~1RESET)
unnamed: R5.1, U1.22 (~2RESET)

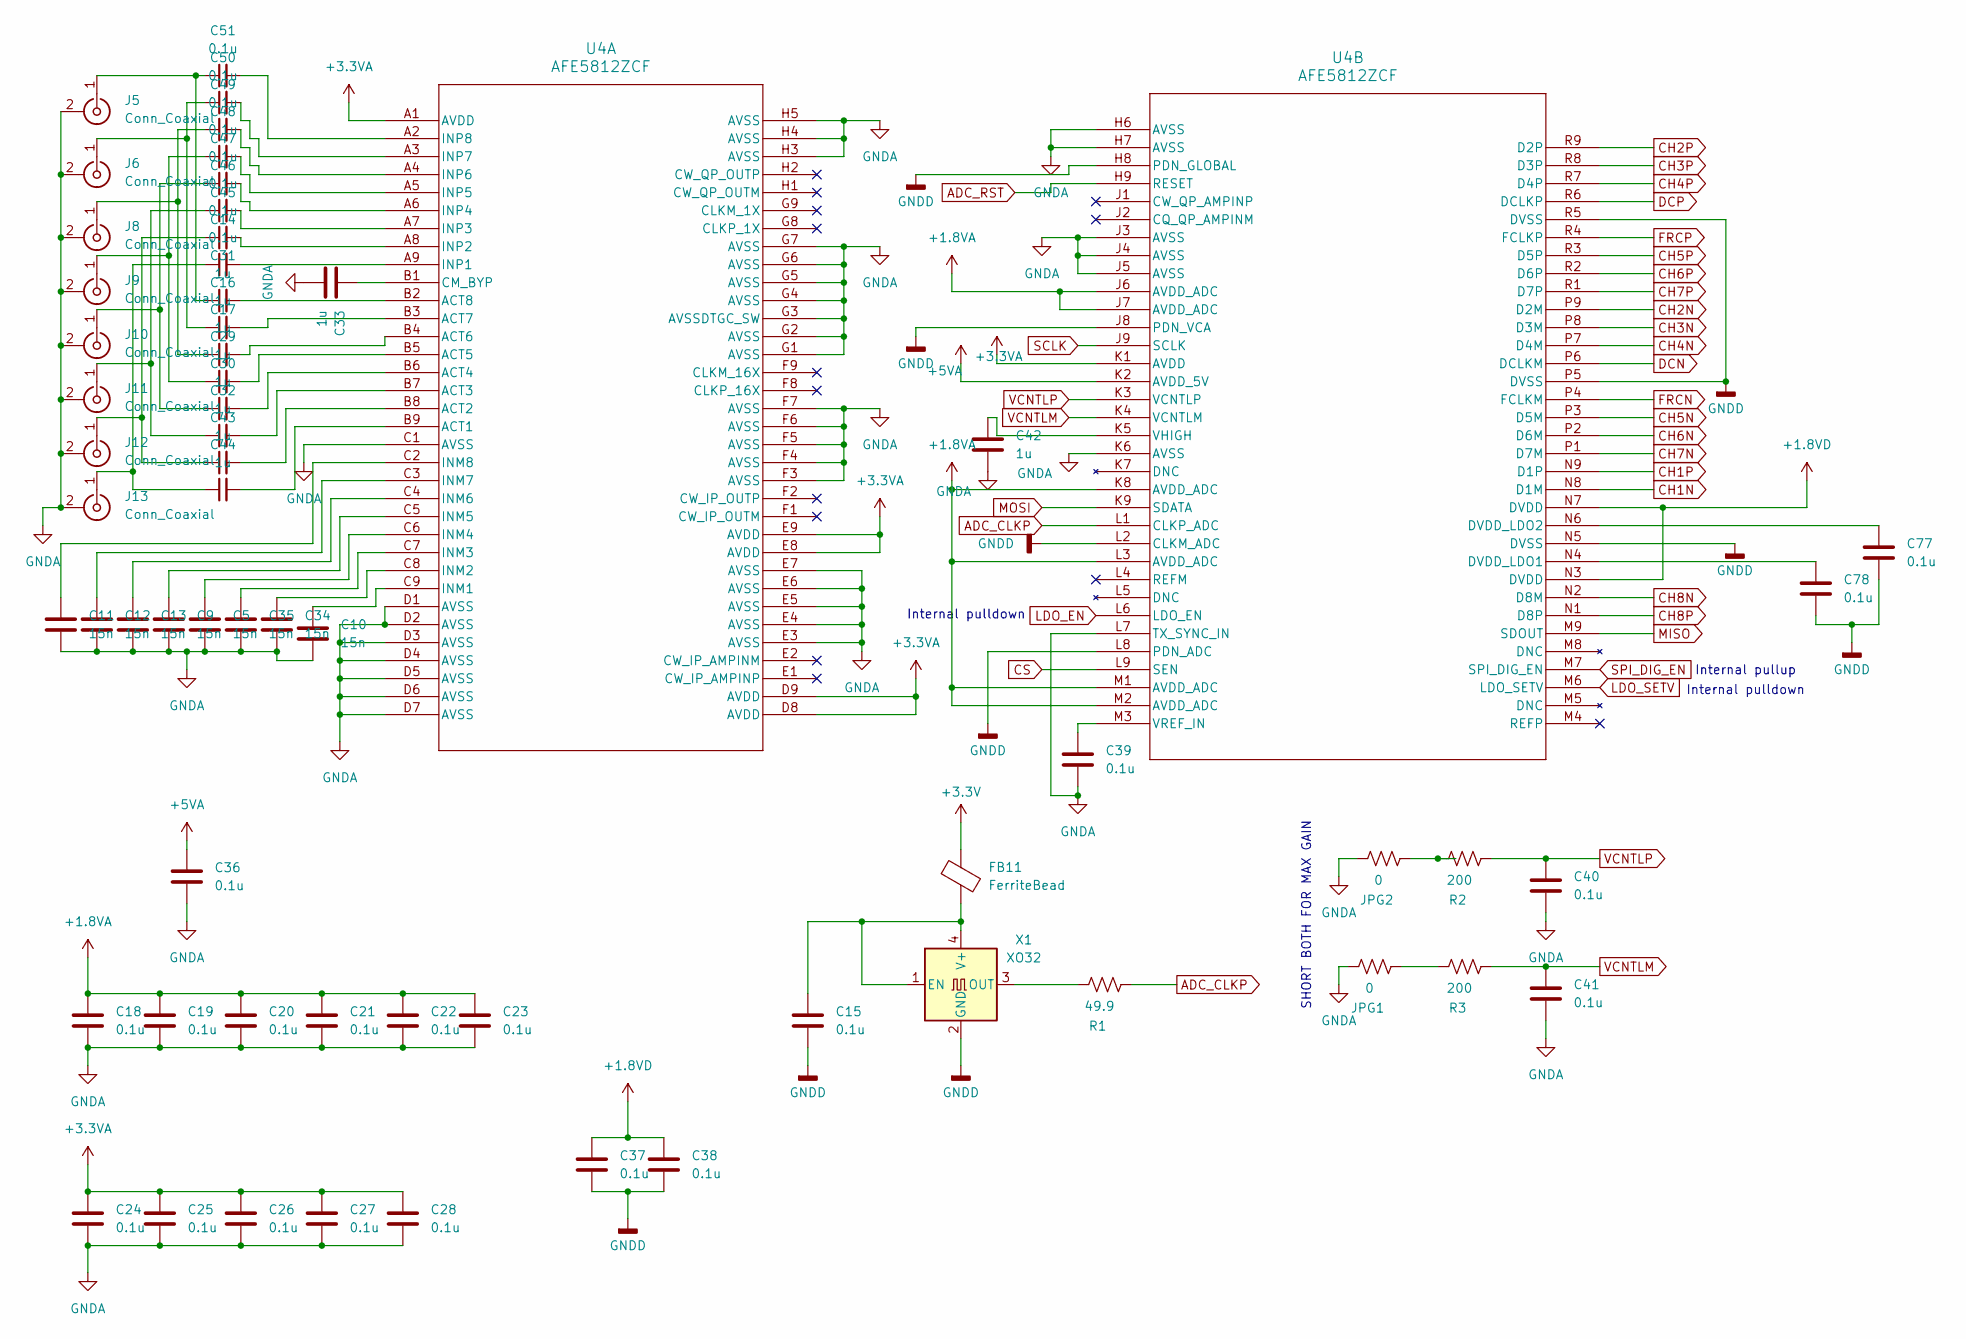
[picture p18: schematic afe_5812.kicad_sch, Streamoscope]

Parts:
C5, C9, C10, C11, C12, C13, C34, C35: 15n; C_0402_1005Metric_Pad0.74x0.62mm_HandSolder
C14, C15, C18, C19, C20, C21, C22, C23, C24, C25, C26, C27, C28, C36, C37, C38, C39, C40, C41, C45, C46, C47, C48, C49, C50, C51, C77, C78: 0.1u; C_0402_1005Metric_Pad0.74x0.62mm_HandSolder
C16, C17, C29, C30, C31, C32, C33, C42, C43, C44: 1u; C_0402_1005Metric_Pad0.74x0.62mm_HandSolder
FB11: FerriteBead; L_0402_1005Metric
J5, J6, J8, J9, J10, J11, J12, J13: Conn_Coaxial; SMA_Amphenol_132134_Vertical
JPG1, JPG2: 0; R_0402_1005Metric_Pad0.72x0.64mm_HandSolder
R1: 49.9; R_0402_1005Metric_Pad0.72x0.64mm_HandSolder
R2, R3: 200; R_0402_1005Metric_Pad0.72x0.64mm_HandSolder
U4: AFE5812ZCF; ZCF135_TEX_NO_PASTE
X1: XO32; Oscillator_SMD_Abracon_ASV-4Pin_7.0x5.1mm

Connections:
+1.8VA: C18.1, C19.1, C20.1, C21.1, C22.1, C23.1, U4.J6 (AVDD_ADC), U4.J7 (AVDD_ADC), U4.K8 (AVDD_ADC), U4.L3 (AVDD_ADC), U4.M1 (AVDD_ADC), U4.M2 (AVDD_ADC); also elsewhere on the board
+1.8VD: C37.1, C38.1, U4.N3 (DVDD), U4.N7 (DVDD); also elsewhere on the board
+3.3V: FB11.1; also elsewhere on the board
+3.3VA: C24.1, C25.1, C26.1, C27.1, C28.1, U4.A1 (AVDD), U4.D8 (AVDD), U4.D9 (AVDD), U4.E8 (AVDD), U4.E9 (AVDD), U4.K1 (AVDD); also elsewhere on the board
+5VA: C36.1, U4.K2 (AVDD_5V); also elsewhere on the board
ADC_CLKP: R1.2, U4.L1 (CLKP_ADC)
ADC_RST: U4.H9 (RESET); also elsewhere on the board
CH1N: U4.N8 (D1M); also elsewhere on the board
CH1P: U4.N9 (D1P); also elsewhere on the board
CH2N: U4.P9 (D2M); also elsewhere on the board
CH2P: U4.R9 (D2P); also elsewhere on the board
CH3N: U4.P8 (D3M); also elsewhere on the board
CH3P: U4.R8 (D3P); also elsewhere on the board
CH4N: U4.P7 (D4M); also elsewhere on the board
CH4P: U4.R7 (D4P); also elsewhere on the board
CH5N: U4.P3 (D5M); also elsewhere on the board
CH5P: U4.R3 (D5P); also elsewhere on the board
CH6N: U4.P2 (D6M); also elsewhere on the board
CH6P: U4.R2 (D6P); also elsewhere on the board
CH7N: U4.P1 (D7M); also elsewhere on the board
CH7P: U4.R1 (D7P); also elsewhere on the board
CH8N: U4.N2 (D8M); also elsewhere on the board
CH8P: U4.N1 (D8P); also elsewhere on the board
CS: U4.L9 (SEN); also elsewhere on the board
DCN: U4.P6 (DCLKM); also elsewhere on the board
DCP: U4.R6 (DCLKP); also elsewhere on the board
FRCN: U4.P4 (FCLKM); also elsewhere on the board
FRCP: U4.R4 (FCLKP); also elsewhere on the board
GND: C5.1, C9.1, C10.1, C11.1, C12.1, C13.1, C15.2, C18.2, C19.2, C20.2, C21.2, C22.2, C23.2, C24.2, C25.2, C26.2, C27.2, C28.2, C33.1, C34.1, C35.1, C36.2, C37.2, C38.2, C39.2, C40.2, C41.2, C42.1, C77.2, C78.2, J5.2 (Ext), J6.2 (Ext), J8.2 (Ext), J9.2 (Ext), J10.2 (Ext), J11.2 (Ext), J12.2 (Ext), J13.2 (Ext), JPG1.1, JPG2.1, U4.C1 (AVSS), U4.D1 (AVSS), U4.D2 (AVSS), U4.D3 (AVSS), U4.D4 (AVSS), U4.D5 (AVSS), U4.D6 (AVSS), U4.D7 (AVSS), U4.E3 (AVSS), U4.E4 (AVSS), U4.E5 (AVSS), U4.E6 (AVSS), U4.E7 (AVSS), U4.F3 (AVSS), U4.F4 (AVSS), U4.F5 (AVSS), U4.F6 (AVSS), U4.F7 (AVSS), U4.G1 (AVSS), U4.G2 (AVSS), U4.G3 (AVSSDTGC_SW), U4.G4 (AVSS), U4.G5 (AVSS), U4.G6 (AVSS), U4.G7 (AVSS), U4.H3 (AVSS), U4.H4 (AVSS), U4.H5 (AVSS), U4.H6 (AVSS), U4.H7 (AVSS), U4.H8 (PDN_GLOBAL), U4.J3 (AVSS), U4.J4 (AVSS), U4.J5 (AVSS), U4.J8 (PDN_VCA), U4.K6 (AVSS), U4.L2 (CLKM_ADC), U4.L7 (TX_SYNC_IN), U4.L8 (PDN_ADC), U4.N5 (DVSS), U4.P5 (DVSS), U4.R5 (DVSS), X1.2 (GND); also elsewhere on the board
LDO_EN: U4.L6 (LDO_EN); also elsewhere on the board
LDO_SETV: U4.M6 (LDO_SETV); also elsewhere on the board
MISO: U4.M9 (SDOUT); also elsewhere on the board
MOSI: U4.K9 (SDATA); also elsewhere on the board
unnamed: C31.1, C51.1, J5.1 (In)
unnamed: C16.1, C50.1, J6.1 (In)
unnamed: C17.1, C49.1, J8.1 (In)
unnamed: C29.1, C48.1, J9.1 (In)
unnamed: C30.1, C47.1, J10.1 (In)
unnamed: C32.1, C46.1, J11.1 (In)
unnamed: C43.1, C45.1, J12.1 (In)
unnamed: C14.1, C44.1, J13.1 (In)
unnamed: JPG1.2, R3.1
unnamed: JPG2.2, R2.1
unnamed: C44.2, U4.B9 (ACT1)
unnamed: C43.2, U4.B8 (ACT2)
unnamed: C32.2, U4.B7 (ACT3)
unnamed: C30.2, U4.B6 (ACT4)
unnamed: C29.2, U4.B5 (ACT5)
unnamed: C17.2, U4.B4 (ACT6)
unnamed: C16.2, U4.B3 (ACT7)
unnamed: C31.2, U4.B2 (ACT8)
unnamed: C33.2, U4.B1 (CM_BYP)
unnamed: C10.2, U4.C9 (INM1)
unnamed: C34.2, U4.C8 (INM2)
unnamed: C35.2, U4.C7 (INM3)
unnamed: C5.2, U4.C6 (INM4)
unnamed: C9.2, U4.C5 (INM5)
unnamed: C13.2, U4.C4 (INM6)
unnamed: C12.2, U4.C3 (INM7)
unnamed: C11.2, U4.C2 (INM8)
unnamed: C14.2, U4.A9 (INP1)
unnamed: C45.2, U4.A8 (INP2)
unnamed: C46.2, U4.A7 (INP3)
unnamed: C47.2, U4.A6 (INP4)
unnamed: C48.2, U4.A5 (INP5)
unnamed: C49.2, U4.A4 (INP6)
unnamed: C50.2, U4.A3 (INP7)
unnamed: C51.2, U4.A2 (INP8)
unnamed: C78.1, U4.N4 (DVDD_LDO1)
unnamed: C77.1, U4.N6 (DVDD_LDO2)
unnamed: C42.2, U4.K5 (VHIGH)
unnamed: C39.1, U4.M3 (VREF_IN)
unnamed: C15.1, FB11.2, X1.1 (EN), X1.4 (V+)
unnamed: R1.1, X1.3 (OUT)
SCLK: U4.J9 (SCLK); also elsewhere on the board
SPI_DIG_EN: U4.M7 (SPI_DIG_EN); also elsewhere on the board
VCNTLM: C41.1, R3.2, U4.K4 (VCNTLM)
VCNTLP: C40.1, R2.2, U4.K3 (VCNTLP)

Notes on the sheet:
Internal pullup
Internal pulldown
SHORT BOTH FOR MAX GAIN

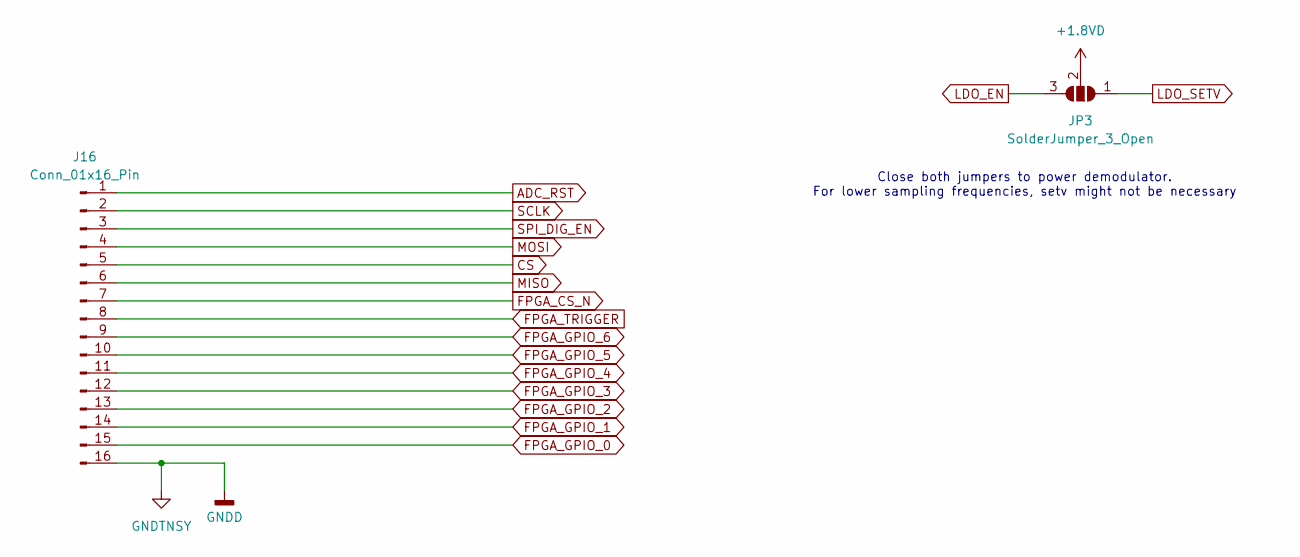
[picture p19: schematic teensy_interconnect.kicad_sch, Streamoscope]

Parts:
J16: Conn_01x16_Pin; PinHeader_1x16_P2.54mm_Vertical
JP3: SolderJumper_3_Open; SolderJumper-3_P1.3mm_Open_Pad1.0x1.5mm

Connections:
+1.8VD: JP3.2 (C); also elsewhere on the board
ADC_RST: J16.1; also elsewhere on the board
CS: J16.5; also elsewhere on the board
FPGA_CS_N: J16.7; also elsewhere on the board
FPGA_GPIO_0: J16.15; also elsewhere on the board
FPGA_GPIO_1: J16.14; also elsewhere on the board
FPGA_GPIO_2: J16.13; also elsewhere on the board
FPGA_GPIO_3: J16.12; also elsewhere on the board
FPGA_GPIO_4: J16.11; also elsewhere on the board
FPGA_GPIO_5: J16.10; also elsewhere on the board
FPGA_GPIO_6: J16.9; also elsewhere on the board
FPGA_TRIGGER: J16.8; also elsewhere on the board
GND: J16.16; also elsewhere on the board
LDO_EN: JP3.3 (B); also elsewhere on the board
LDO_SETV: JP3.1 (A); also elsewhere on the board
MISO: J16.6; also elsewhere on the board
MOSI: J16.4; also elsewhere on the board
SCLK: J16.2; also elsewhere on the board
SPI_DIG_EN: J16.3; also elsewhere on the board

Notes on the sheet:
Close both jumpers to power demodulator. For lower sampling frequencies, setv might not be necessary

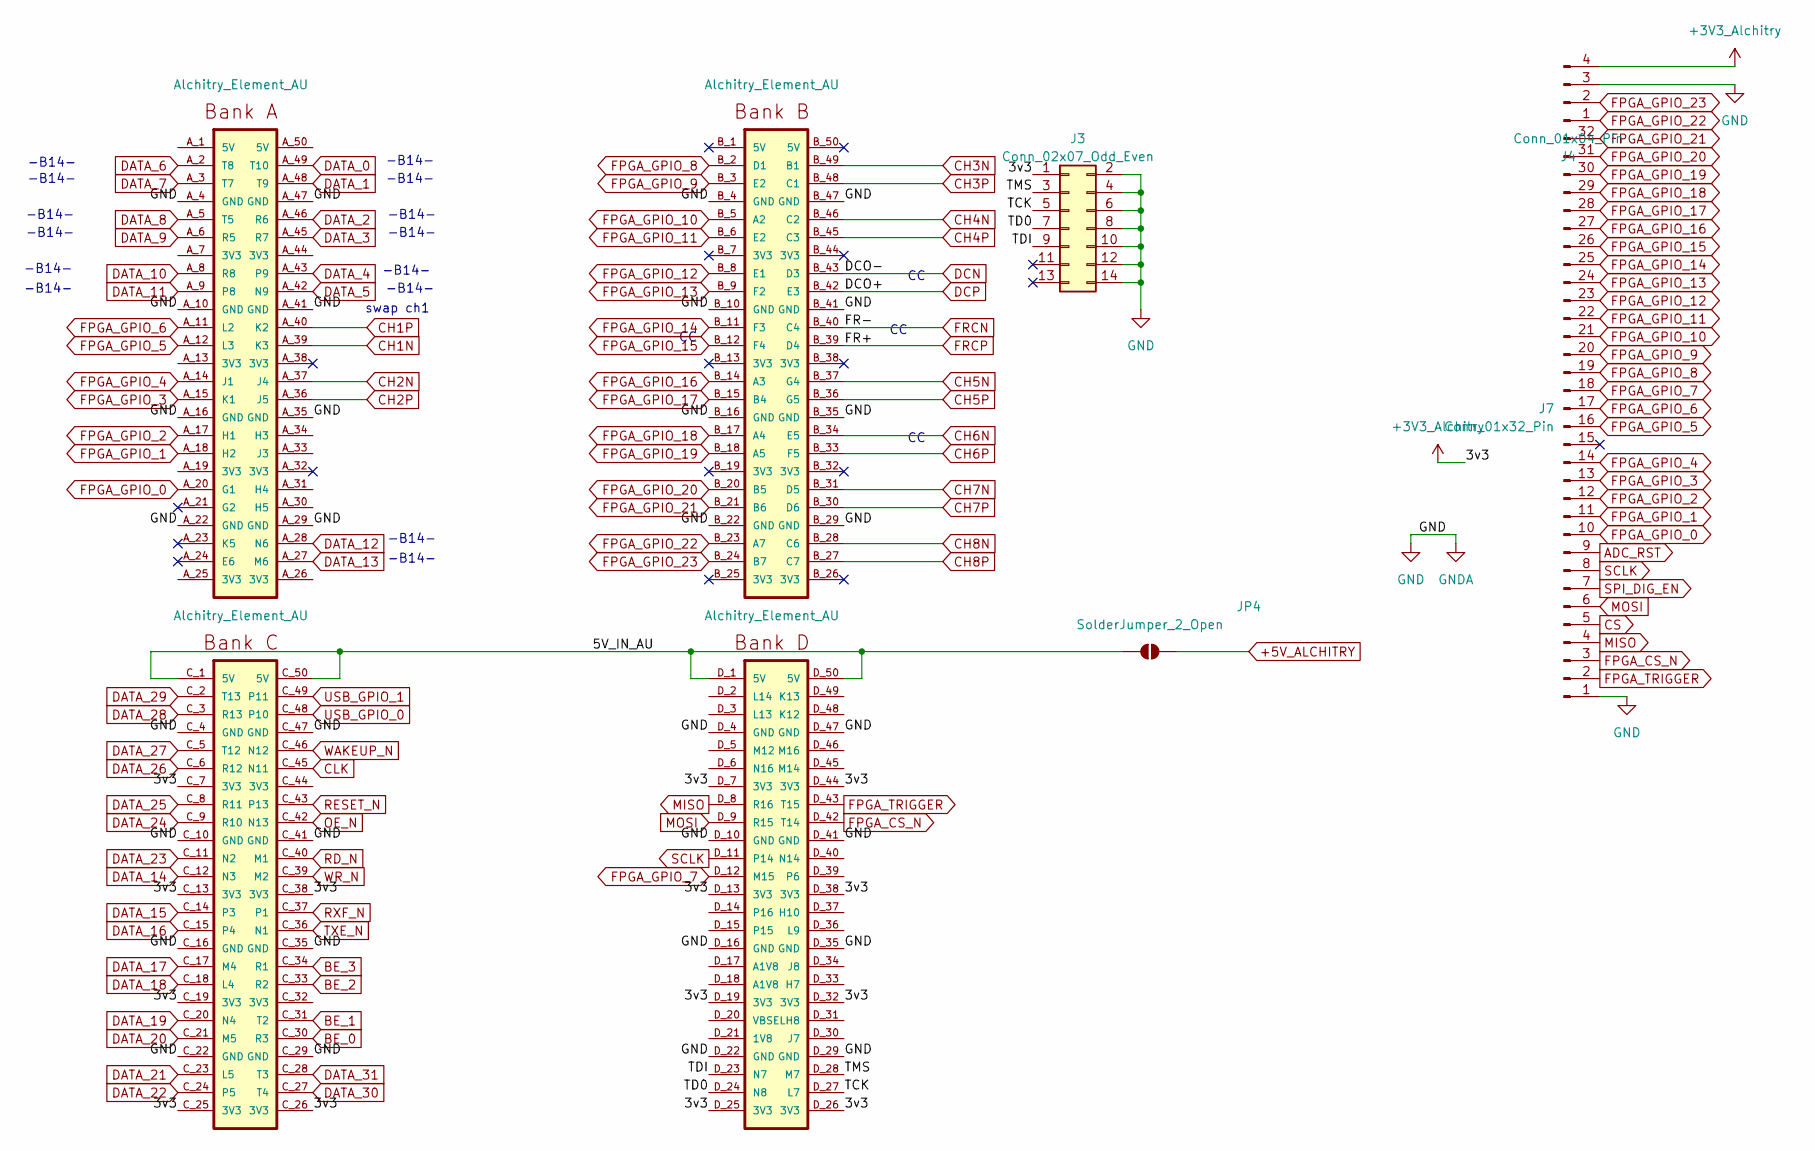
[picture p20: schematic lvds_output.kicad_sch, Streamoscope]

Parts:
B1: Alchitry_Element_AU; Element_no_top
J3: Conn_02x07_Odd_Even; PinSocket_2x07_P2.00mm_Vertical
J4: Conn_01x04_Pin; PinSocket_1x04_P2.54mm_Vertical
J7: Conn_01x32_Pin; PinHeader_1x32_P2.54mm_Vertical
JP4: SolderJumper_2_Open; SolderJumper-2_P1.3mm_Open_Pad1.0x1.5mm

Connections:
+3V3_Alchitry: B1.C_7 (3V3), B1.C_13 (3V3), B1.C_19 (3V3), B1.C_25 (3V3), B1.C_26 (3V3), B1.C_38 (3V3), B1.D_7 (3V3), B1.D_13 (3V3), B1.D_19 (3V3), B1.D_25 (3V3), B1.D_26 (3V3), B1.D_32 (3V3), B1.D_38 (3V3), B1.D_44 (3V3), J3.1, J4.4; also elsewhere on the board
+5V_ALCHITRY: JP4.2 (B); also elsewhere on the board
/lvds_output/5V_IN_AU: B1.C_1 (5V), B1.C_50 (5V), B1.D_1 (5V), B1.D_50 (5V), JP4.1 (A)
/lvds_output/TCK: B1.D_27 (L7), J3.5
/lvds_output/TD0: B1.D_24 (N8), J3.7
/lvds_output/TDI: B1.D_23 (N7), J3.9
/lvds_output/TMS: B1.D_28 (M7), J3.3
ADC_RST: J7.9; also elsewhere on the board
BE_0: B1.C_30 (R3); also elsewhere on the board
BE_1: B1.C_31 (T2); also elsewhere on the board
BE_2: B1.C_33 (R2); also elsewhere on the board
BE_3: B1.C_34 (R1); also elsewhere on the board
CH1N: B1.A_39 (K3); also elsewhere on the board
CH1P: B1.A_40 (K2); also elsewhere on the board
CH2N: B1.A_37 (J4); also elsewhere on the board
CH2P: B1.A_36 (J5); also elsewhere on the board
CH3N: B1.B_49 (B1); also elsewhere on the board
CH3P: B1.B_48 (C1); also elsewhere on the board
CH4N: B1.B_46 (C2); also elsewhere on the board
CH4P: B1.B_45 (C3); also elsewhere on the board
CH5N: B1.B_37 (G4); also elsewhere on the board
CH5P: B1.B_36 (G5); also elsewhere on the board
CH6N: B1.B_34 (E5); also elsewhere on the board
CH6P: B1.B_33 (F5); also elsewhere on the board
CH7N: B1.B_31 (D5); also elsewhere on the board
CH7P: B1.B_30 (D6); also elsewhere on the board
CH8N: B1.B_28 (C6); also elsewhere on the board
CH8P: B1.B_27 (C7); also elsewhere on the board
CLK: B1.C_45 (N11); also elsewhere on the board
CS: J7.5; also elsewhere on the board
DATA_0: B1.A_49 (T10); also elsewhere on the board
DATA_1: B1.A_48 (T9); also elsewhere on the board
DATA_2: B1.A_46 (R6); also elsewhere on the board
DATA_3: B1.A_45 (R7); also elsewhere on the board
DATA_4: B1.A_43 (P9); also elsewhere on the board
DATA_5: B1.A_42 (N9); also elsewhere on the board
DATA_6: B1.A_2 (T8); also elsewhere on the board
DATA_7: B1.A_3 (T7); also elsewhere on the board
DATA_8: B1.A_5 (T5); also elsewhere on the board
DATA_9: B1.A_6 (R5); also elsewhere on the board
DATA_10: B1.A_8 (R8); also elsewhere on the board
DATA_11: B1.A_9 (P8); also elsewhere on the board
DATA_12: B1.A_28 (N6); also elsewhere on the board
DATA_13: B1.A_27 (M6); also elsewhere on the board
DATA_14: B1.C_12 (N3); also elsewhere on the board
DATA_15: B1.C_14 (P3); also elsewhere on the board
DATA_16: B1.C_15 (P4); also elsewhere on the board
DATA_17: B1.C_17 (M4); also elsewhere on the board
DATA_18: B1.C_18 (L4); also elsewhere on the board
DATA_19: B1.C_20 (N4); also elsewhere on the board
DATA_20: B1.C_21 (M5); also elsewhere on the board
DATA_21: B1.C_23 (L5); also elsewhere on the board
DATA_22: B1.C_24 (P5); also elsewhere on the board
DATA_23: B1.C_11 (N2); also elsewhere on the board
DATA_24: B1.C_9 (R10); also elsewhere on the board
DATA_25: B1.C_8 (R11); also elsewhere on the board
DATA_26: B1.C_6 (R12); also elsewhere on the board
DATA_27: B1.C_5 (T12); also elsewhere on the board
DATA_28: B1.C_3 (R13); also elsewhere on the board
DATA_29: B1.C_2 (T13); also elsewhere on the board
DATA_30: B1.C_27 (T4); also elsewhere on the board
DATA_31: B1.C_28 (T3); also elsewhere on the board
DCN: B1.B_43 (D3); also elsewhere on the board
DCP: B1.B_42 (E3); also elsewhere on the board
FPGA_CS_N: B1.D_42 (T14), J7.3; also elsewhere on the board
FPGA_GPIO_0: B1.A_20 (G1), J7.10; also elsewhere on the board
FPGA_GPIO_1: B1.A_18 (H2), J7.11; also elsewhere on the board
FPGA_GPIO_2: B1.A_17 (H1), J7.12; also elsewhere on the board
FPGA_GPIO_3: B1.A_15 (K1), J7.13; also elsewhere on the board
FPGA_GPIO_4: B1.A_14 (J1), J7.14; also elsewhere on the board
FPGA_GPIO_5: B1.A_12 (L3), J7.16; also elsewhere on the board
FPGA_GPIO_6: B1.A_11 (L2), J7.17; also elsewhere on the board
FPGA_GPIO_7: B1.D_12 (M15), J7.18
FPGA_GPIO_8: B1.B_2 (D1), J7.19
FPGA_GPIO_9: B1.B_3 (E2), J7.20
FPGA_GPIO_10: B1.B_5 (A2), J7.21
FPGA_GPIO_11: B1.B_6 (E2), J7.22
FPGA_GPIO_12: B1.B_8 (E1), J7.23
FPGA_GPIO_13: B1.B_9 (F2), J7.24
FPGA_GPIO_14: B1.B_11 (F3), J7.25
FPGA_GPIO_15: B1.B_12 (F4), J7.26
FPGA_GPIO_16: B1.B_14 (A3), J7.27
FPGA_GPIO_17: B1.B_15 (B4), J7.28
FPGA_GPIO_18: B1.B_17 (A4), J7.29
FPGA_GPIO_19: B1.B_18 (A5), J7.30
FPGA_GPIO_20: B1.B_20 (B5), J7.31
FPGA_GPIO_21: B1.B_21 (B6), J7.32
FPGA_GPIO_22: B1.B_23 (A7), J4.1
FPGA_GPIO_23: B1.B_24 (B7), J4.2
FPGA_TRIGGER: B1.D_43 (T15), J7.2; also elsewhere on the board
FRCN: B1.B_40 (C4); also elsewhere on the board
FRCP: B1.B_39 (D4); also elsewhere on the board
GND: B1.A_4 (GND), B1.A_10 (GND), B1.A_16 (GND), B1.A_22 (GND), B1.A_29 (GND), B1.A_35 (GND), B1.A_41 (GND), B1.A_47 (GND), B1.B_4 (GND), B1.B_10 (GND), B1.B_16 (GND), B1.B_22 (GND), B1.B_29 (GND), B1.B_35 (GND), B1.B_41 (GND), B1.B_47 (GND), B1.C_4 (GND), B1.C_10 (GND), B1.C_16 (GND), B1.C_22 (GND), B1.C_29 (GND), B1.C_35 (GND), B1.C_41 (GND), B1.C_47 (GND), B1.D_4 (GND), B1.D_10 (GND), B1.D_16 (GND), B1.D_22 (GND), B1.D_29 (GND), B1.D_35 (GND), B1.D_41 (GND), B1.D_47 (GND), J3.2, J3.4, J3.6, J3.8, J3.10, J3.12, J3.14, J4.3, J7.1; also elsewhere on the board
MISO: B1.D_8 (R16), J7.4; also elsewhere on the board
MOSI: B1.D_9 (R15), J7.6; also elsewhere on the board
OE_N: B1.C_42 (N13); also elsewhere on the board
RD_N: B1.C_40 (M1); also elsewhere on the board
RESET_N: B1.C_43 (P13); also elsewhere on the board
RXF_N: B1.C_37 (P1); also elsewhere on the board
SCLK: B1.D_11 (P14), J7.8; also elsewhere on the board
SPI_DIG_EN: J7.7; also elsewhere on the board
TXE_N: B1.C_36 (N1); also elsewhere on the board
USB_GPIO_0: B1.C_48 (P10); also elsewhere on the board
USB_GPIO_1: B1.C_49 (P11); also elsewhere on the board
WAKEUP_N: B1.C_46 (N12); also elsewhere on the board
WR_N: B1.C_39 (M2); also elsewhere on the board

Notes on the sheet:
-B14-
swap ch1

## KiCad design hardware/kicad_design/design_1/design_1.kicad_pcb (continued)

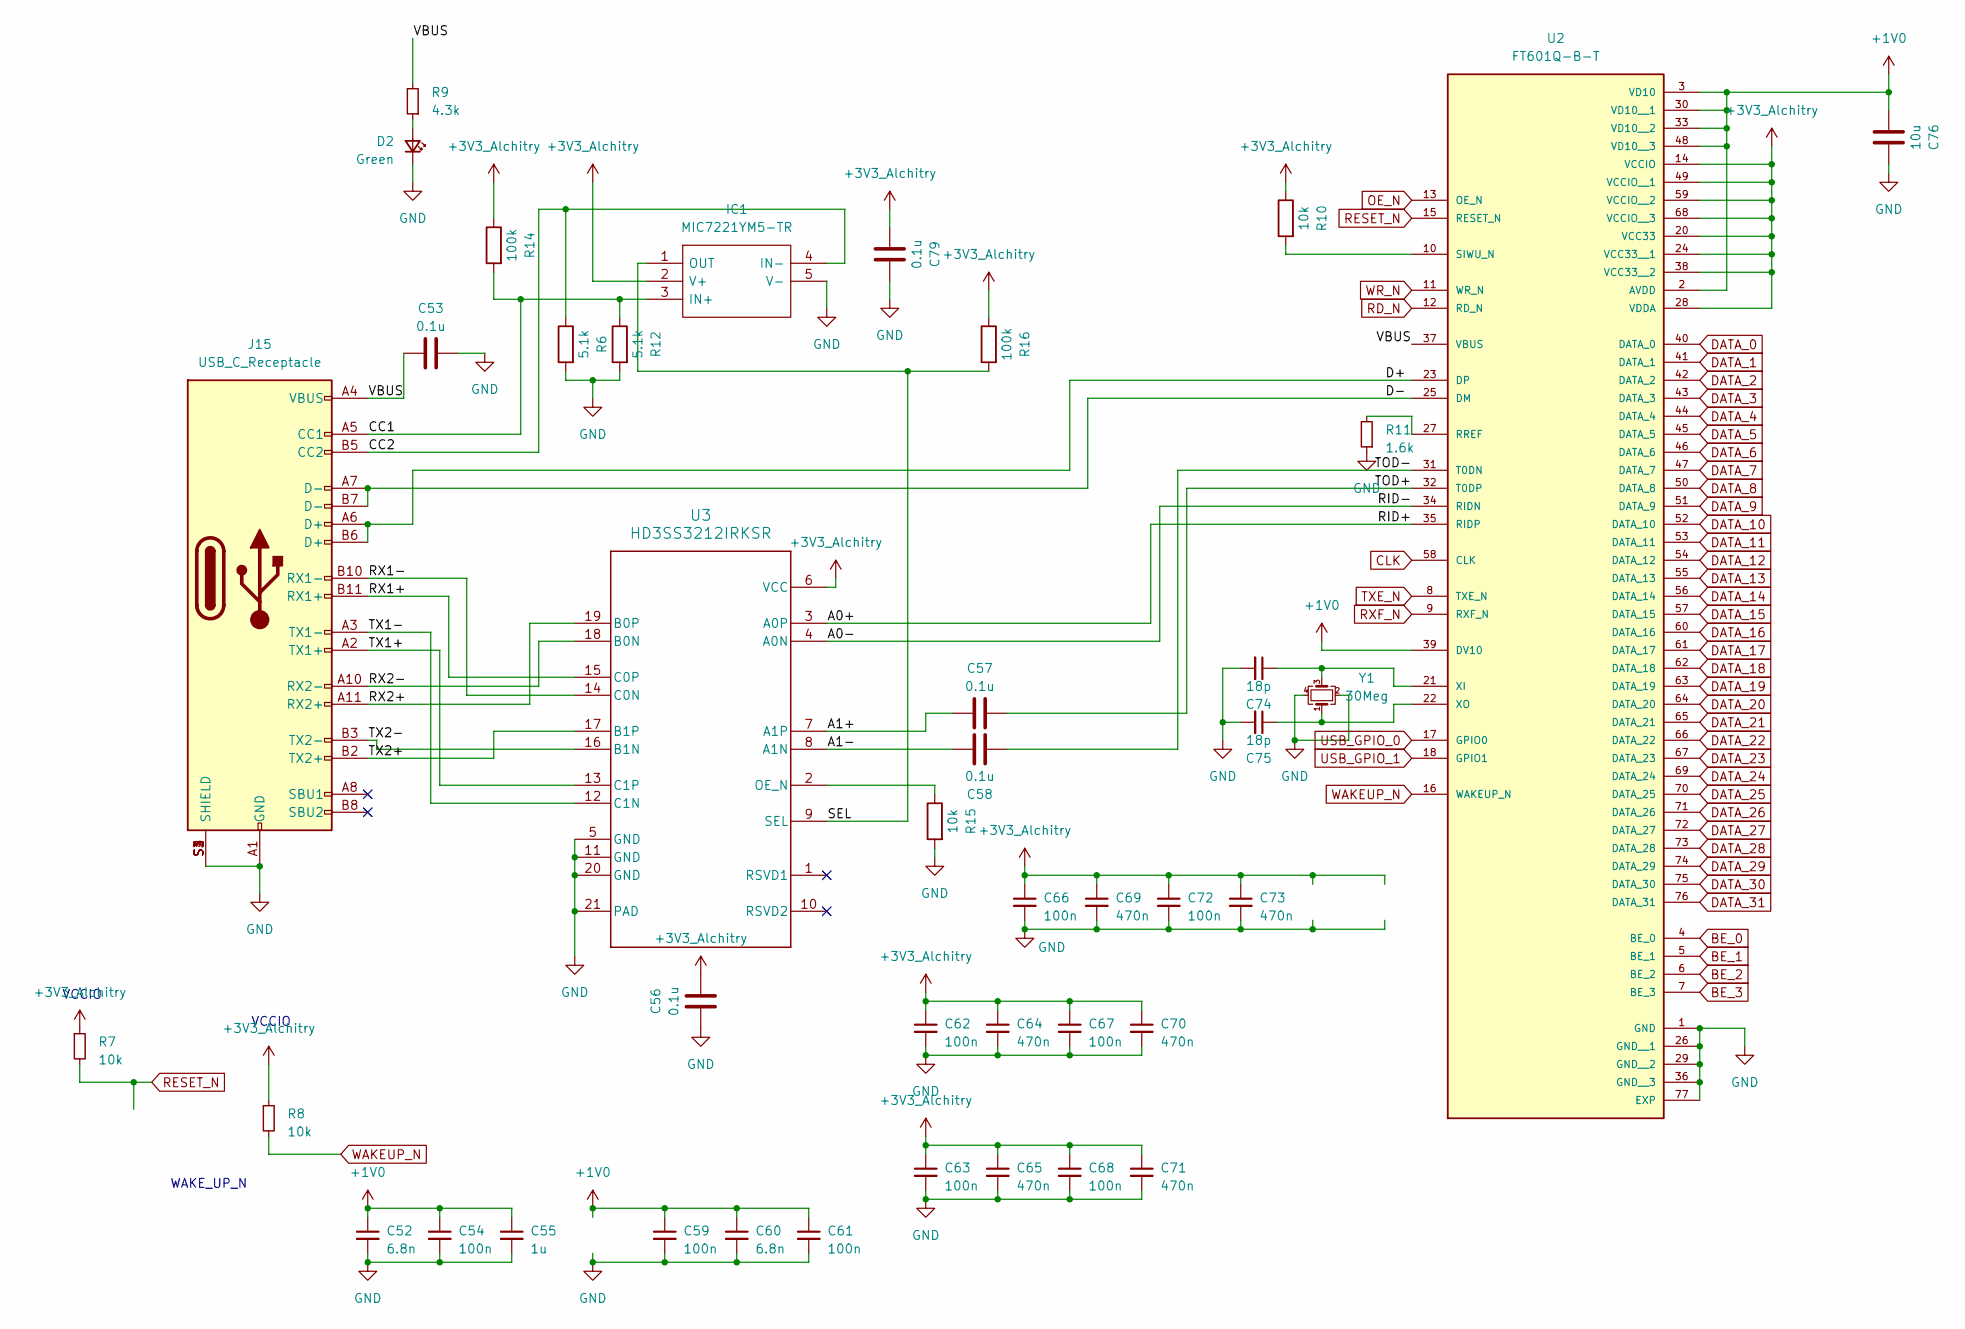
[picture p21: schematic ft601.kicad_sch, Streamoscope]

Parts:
C52, C60: 6.8n; C_0402_1005Metric_Pad0.74x0.62mm_HandSolder
C53, C56, C57, C58, C79: 0.1u; C_0402_1005Metric_Pad0.74x0.62mm_HandSolder
C54, C59, C61, C62, C63, C66, C67, C68, C72: 100n; C_0402_1005Metric_Pad0.74x0.62mm_HandSolder
C55: 1u; C_0402_1005Metric_Pad0.74x0.62mm_HandSolder
C64, C65, C69, C70, C71, C73: 470n; C_0402_1005Metric_Pad0.74x0.62mm_HandSolder
C74, C75: 18p; C_0402_1005Metric_Pad0.74x0.62mm_HandSolder
C76: 10u; C_0402_1005Metric_Pad0.74x0.62mm_HandSolder
D2: Green; LED_0603_1608Metric
IC1: MIC7221YM5-TR; SOT95P280X130-5N; Mouser Part Number 998-MIC7221YM5TR
J15: USB_C_Receptacle; AMPHENOL_12401899E412A
R6, R12: 5.1k; R_0402_1005Metric_Pad0.72x0.64mm_HandSolder
R7, R8, R10, R15: 10k; R_0402_1005Metric_Pad0.72x0.64mm_HandSolder
R9: 4.3k; R_0402_1005Metric_Pad0.72x0.64mm_HandSolder
R11: 1.6k; R_0402_1005Metric_Pad0.72x0.64mm_HandSolder
R14, R16: 100k; R_0402_1005Metric_Pad0.72x0.64mm_HandSolder
U2: FT601Q-B-T; QFN40P900X900X100-77N; PARTREV 1.05
U3: HD3SS3212IRKSR; SN74HCS541RKSR
Y1: 30Meg; Crystal_SMD_3225-4Pin_3.2x2.5mm; MPN 830059646

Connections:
+1V0: C52.1, C54.1, C55.1, C59.1, C60.1, C61.1, C76.1, U2.2 (AVDD), U2.3 (VD10), U2.30 (VD10__1), U2.33 (VD10__2), U2.39 (DV10), U2.48 (VD10__3)
+3V3_Alchitry: C56.2, C62.1, C63.1, C64.1, C65.1, C66.1, C67.1, C68.1, C69.1, C70.1, C71.1, C72.1, C73.1, C79.1, IC1.2 (V+), R7.1, R8.1, R10.1, R14.1, R16.1, U2.14 (VCCIO), U2.20 (VCC33), U2.24 (VCC33__1), U2.28 (VDDA), U2.38 (VCC33__2), U2.49 (VCCIO__1), U2.59 (VCCIO__2), U2.68 (VCCIO__3), U3.6 (VCC); also elsewhere on the board
/ft601/A0+: U2.35 (RIDP), U3.3 (A0P)
/ft601/A0-: U2.34 (RIDN), U3.4 (A0N)
/ft601/A1+: C57.1, U3.7 (A1P)
/ft601/A1-: C58.1, U3.8 (A1N)
/ft601/CC1: IC1.3 (IN+), J15.A5 (CC1), R12.1, R14.2
/ft601/CC2: IC1.4 (IN-), J15.B5 (CC2), R6.1
/ft601/D+: J15.A6 (D+), J15.B6 (D+), U2.23 (DP)
/ft601/D-: J15.A7 (D-), J15.B7 (D-), U2.25 (DM)
/ft601/RX1+: J15.B11 (RX1+), U3.15 (C0P)
/ft601/RX1-: J15.B10 (RX1-), U3.14 (C0N)
/ft601/RX2+: J15.A11 (RX2+), U3.19 (B0P)
/ft601/RX2-: J15.A10 (RX2-), U3.18 (B0N)
/ft601/SEL: IC1.1 (OUT), R16.2, U3.9 (SEL)
/ft601/TOD+: C57.2, U2.32 (T0DP)
/ft601/TOD-: C58.2, U2.31 (T0DN)
/ft601/TX1+: J15.A2 (TX1+), U3.13 (C1P)
/ft601/TX1-: J15.A3 (TX1-), U3.12 (C1N)
/ft601/TX2+: J15.B2 (TX2+), U3.17 (B1P)
/ft601/TX2-: J15.B3 (TX2-), U3.16 (B1N)
/ft601/VBUS: C53.1, J15.A4 (VBUS), J15.A9 (VBUS), J15.B4 (VBUS), J15.B9 (VBUS), R9.2, U2.37 (VBUS)
BE_0: U2.4 (BE_0); also elsewhere on the board
BE_1: U2.5 (BE_1); also elsewhere on the board
BE_2: U2.6 (BE_2); also elsewhere on the board
BE_3: U2.7 (BE_3); also elsewhere on the board
CLK: U2.58 (CLK); also elsewhere on the board
DATA_0: U2.40 (DATA_0); also elsewhere on the board
DATA_1: U2.41 (DATA_1); also elsewhere on the board
DATA_2: U2.42 (DATA_2); also elsewhere on the board
DATA_3: U2.43 (DATA_3); also elsewhere on the board
DATA_4: U2.44 (DATA_4); also elsewhere on the board
DATA_5: U2.45 (DATA_5); also elsewhere on the board
DATA_6: U2.46 (DATA_6); also elsewhere on the board
DATA_7: U2.47 (DATA_7); also elsewhere on the board
DATA_8: U2.50 (DATA_8); also elsewhere on the board
DATA_9: U2.51 (DATA_9); also elsewhere on the board
DATA_10: U2.52 (DATA_10); also elsewhere on the board
DATA_11: U2.53 (DATA_11); also elsewhere on the board
DATA_12: U2.54 (DATA_12); also elsewhere on the board
DATA_13: U2.55 (DATA_13); also elsewhere on the board
DATA_14: U2.56 (DATA_14); also elsewhere on the board
DATA_15: U2.57 (DATA_15); also elsewhere on the board
DATA_16: U2.60 (DATA_16); also elsewhere on the board
DATA_17: U2.61 (DATA_17); also elsewhere on the board
DATA_18: U2.62 (DATA_18); also elsewhere on the board
DATA_19: U2.63 (DATA_19); also elsewhere on the board
DATA_20: U2.64 (DATA_20); also elsewhere on the board
DATA_21: U2.65 (DATA_21); also elsewhere on the board
DATA_22: U2.66 (DATA_22); also elsewhere on the board
DATA_23: U2.67 (DATA_23); also elsewhere on the board
DATA_24: U2.69 (DATA_24); also elsewhere on the board
DATA_25: U2.70 (DATA_25); also elsewhere on the board
DATA_26: U2.71 (DATA_26); also elsewhere on the board
DATA_27: U2.72 (DATA_27); also elsewhere on the board
DATA_28: U2.73 (DATA_28); also elsewhere on the board
DATA_29: U2.74 (DATA_29); also elsewhere on the board
DATA_30: U2.75 (DATA_30); also elsewhere on the board
DATA_31: U2.76 (DATA_31); also elsewhere on the board
GND: C52.2, C53.2, C54.2, C55.2, C56.1, C59.2, C60.2, C61.2, C62.2, C63.2, C64.2, C65.2, C66.2, C67.2, C68.2, C69.2, C70.2, C71.2, C72.2, C73.2, C74.2, C75.2, C76.2, C79.2, D2.1 (K), IC1.5 (V-), J15.A1 (GND), J15.A12 (GND), J15.B1 (GND), J15.B12 (GND), J15.S1 (SHIELD), J15.S2 (SHIELD), J15.S3 (SHIELD), J15.S4 (SHIELD), R6.2, R11.1, R12.2, R15.2, U2.1 (GND), U2.26 (GND__1), U2.29 (GND__2), U2.36 (GND__3), U2.77 (EXP), U3.5 (GND), U3.11 (GND), U3.20 (GND), U3.21 (PAD), Y1.2, Y1.4; also elsewhere on the board
unnamed: D2.2 (A), R9.1
unnamed: R11.2, U2.27 (RREF)
unnamed: R10.2, U2.10 (SIWU_N)
unnamed: C74.1, U2.21 (XI), Y1.3
unnamed: C75.1, U2.22 (XO), Y1.1
unnamed: R15.1, U3.2 (OE_N)
OE_N: U2.13 (OE_N); also elsewhere on the board
RD_N: U2.12 (RD_N); also elsewhere on the board
RESET_N: R7.2, U2.15 (RESET_N); also elsewhere on the board
RXF_N: U2.9 (RXF_N); also elsewhere on the board
TXE_N: U2.8 (TXE_N); also elsewhere on the board
USB_GPIO_0: U2.17 (GPIO0); also elsewhere on the board
USB_GPIO_1: U2.18 (GPIO1); also elsewhere on the board
WAKEUP_N: R8.2, U2.16 (WAKEUP_N); also elsewhere on the board
WR_N: U2.11 (WR_N); also elsewhere on the board

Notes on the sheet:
VCCIO
WAKE_UP_N

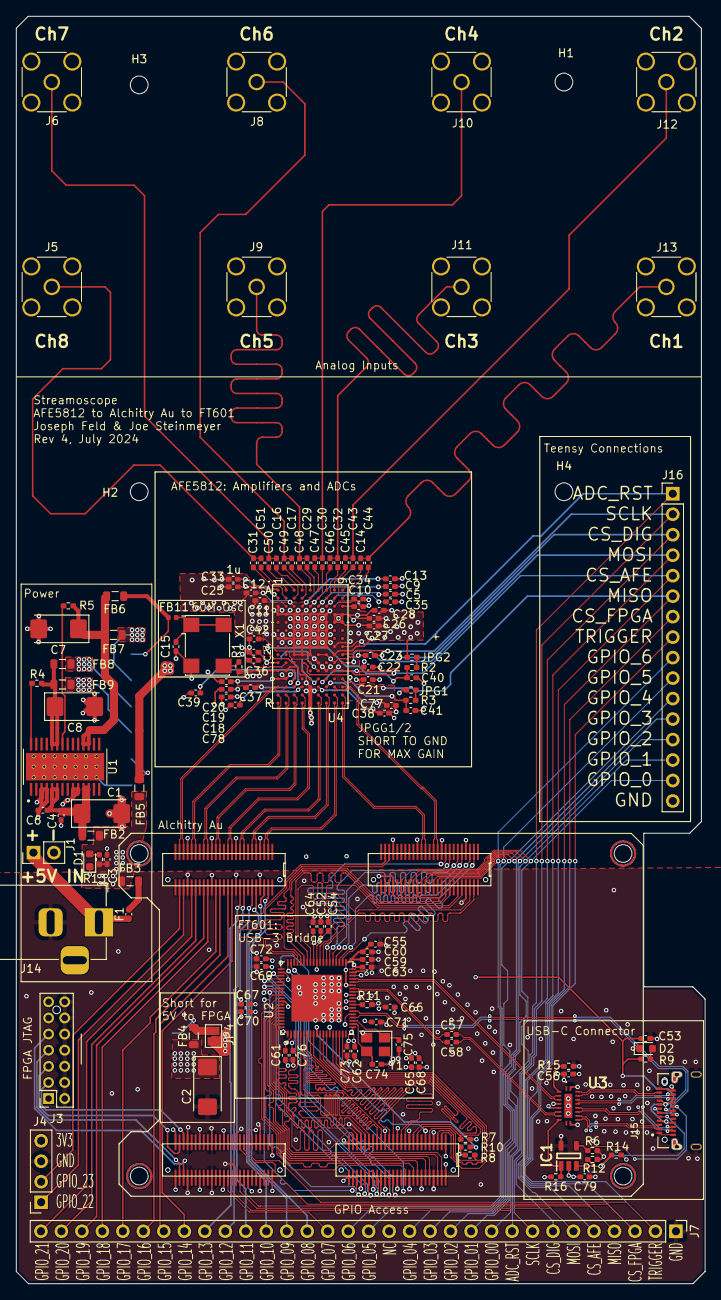
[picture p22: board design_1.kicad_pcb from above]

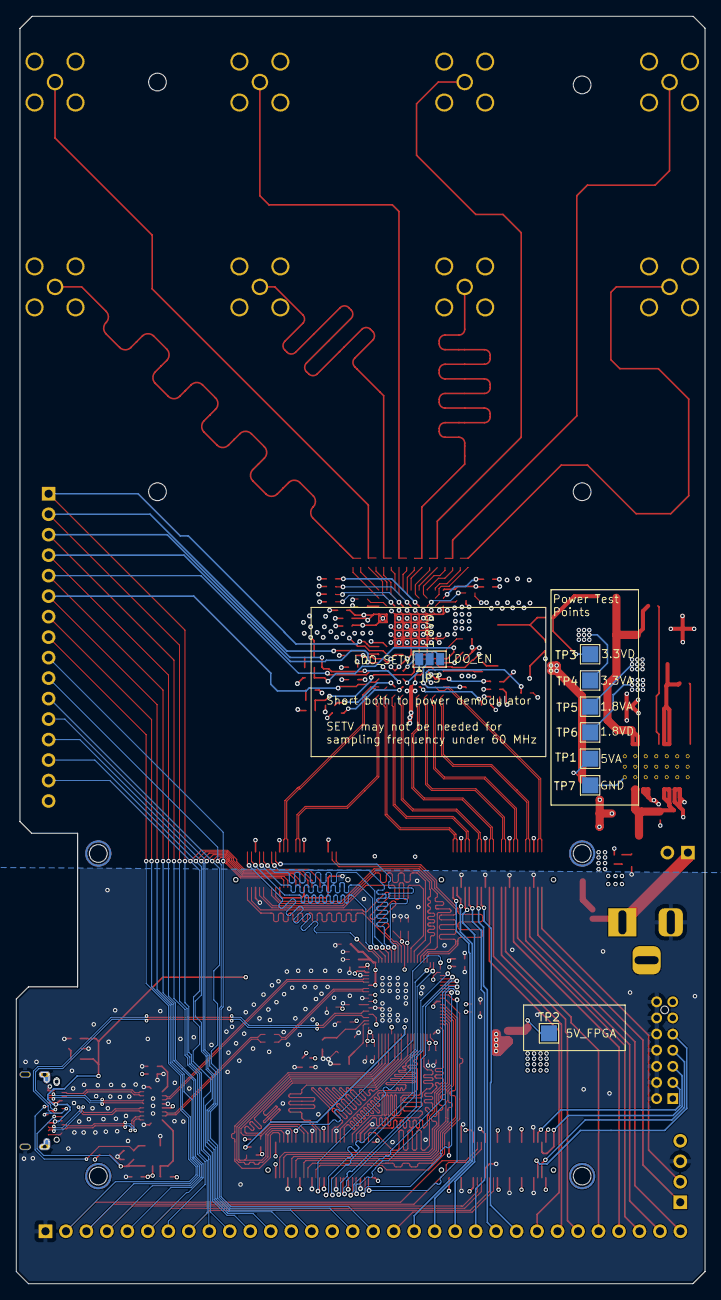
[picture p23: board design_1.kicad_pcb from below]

Board: 4 copper layers, 85.4 x 157.2 mm, 145 parts (9 on the bottom side), 193 nets.

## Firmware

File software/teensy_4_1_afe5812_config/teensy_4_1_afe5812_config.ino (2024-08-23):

#include <SPI.h>

// set pin 10 as the slave select for the digital pot:
const int slaveSelectPin = 10;

//CDC configuration
//MSB to LSB
//see page 5 https://www.ti.com/lit/ds/symlink/cdc7005.pdf?ts=1717427064621
const int word0[4] = { 0b01101010, 0b10100100, 0b00000001, 0b11111100 };
const int word1[4] = { 0b01011011, 0b01000100, 0b00000001, 0b11111101 };
const int word2[4] = { 0b00000000, 0b00000000, 0b00000000, 0b00111010 };
const int word3[4] = { 0b00000000, 0b00000000, 0b00000000, 0b00000011 };
const int* words[4] = { word0, word1, word2, word3 };

const uint8_t AFE_RESET = 3;
const uint8_t AFE_PDN_VCA = 4;
const uint8_t AFE_PDN_ADC = 5;
const uint8_t AFE_PDN_GLOBAL = 6;

const uint8_t AFE_MISO_PIN = 39;
const uint8_t AFE_MOSI_PIN = 26;
const uint8_t AFE_SCK_PIN = 27;
const uint8_t AFE_CE_PIN = 38;

//Joe's SPI bit-bang code
/* Shift a byte out serially with the given frequency in Hz (<= 500kHz) */
void spi_write(uint8_t data_pin, uint8_t clock_pin, uint32_t freq, uint8_t bit_order, uint8_t mode, uint8_t bits, uint32_t val) {
  uint32_t period = (freq >= 500000) ? 1 : (500000 / freq);  // Half clock period in uS
  uint8_t cpol = (mode == SPI_MODE2 || mode == SPI_MODE3);
  uint8_t cpha = (mode == SPI_MODE1 || mode == SPI_MODE3);
  uint8_t sck = cpol ? HIGH : LOW;

  uint8_t i;
  uint32_t start_time;

  // Set clock idle for 2 periods
  digitalWrite(clock_pin, sck);
  delayMicroseconds(period * 4);

  for (i = 0; i < bits; i++) {
    start_time = micros();

    // Shift bit out
    if (bit_order == LSBFIRST)
      digitalWrite(data_pin, !!(val & (1 << i)));
    else
      digitalWrite(data_pin, !!(val & (1 << ((bits - 1) - i))));

    // Toggle clock leading edge
    sck = !sck;
    if (cpha) {
      digitalWrite(clock_pin, sck);
      while (micros() - start_time < period)
        ;
    } else {
      while (micros() - start_time < period)
        ;
      digitalWrite(clock_pin, sck);
    }

    // Toggle clock trailing edge
    start_time = micros();
    sck = !sck;
    if (cpha) {
      digitalWrite(clock_pin, sck);
      while (micros() - start_time < period)
        ;
    } else {
      while (micros() - start_time < period)
        ;
      digitalWrite(clock_pin, sck);
    }
  }
}



void setup() {
  // put your setup code here, to run once:
  pinMode(LED_BUILTIN, OUTPUT);

  pinMode(slaveSelectPin, OUTPUT);
  digitalWrite(slaveSelectPin, HIGH);

  pinMode(AFE_MISO_PIN, INPUT);
  pinMode(AFE_MOSI_PIN, OUTPUT);
  pinMode(AFE_SCK_PIN, OUTPUT);
  pinMode(AFE_CE_PIN, OUTPUT);

  pinMode(AFE_RESET, OUTPUT);
  pinMode(AFE_PDN_VCA, OUTPUT);
  pinMode(AFE_PDN_ADC, OUTPUT);
  pinMode(AFE_PDN_GLOBAL, OUTPUT);


  // initialize SPI:
  // SPI1.begin();
  digitalWrite(AFE_PDN_VCA, 0);
  digitalWrite(AFE_PDN_ADC, 0);
  digitalWrite(AFE_PDN_GLOBAL, 0);
  digitalWrite(AFE_SCK_PIN, 1);
  digitalWrite(AFE_RESET, 0);
  digitalWrite(AFE_CE_PIN, 1);
  delay(1);
  digitalWrite(AFE_RESET, 1);
  delay(1);
  digitalWrite(AFE_RESET, 0);
  
  delay(10);

  // configureCDC7005();
  loopbackAFE();
}

void loop() {
  // put your main code here, to run repeatedly:
  // digitalWrite(LED_BUILTIN, HIGH);  // turn the LED on (HIGH is the voltage level)
  // delay(500);                       // wait for a second
  // digitalWrite(LED_BUILTIN, LOW);   // turn the LED off by making the voltage LOW
  // delay(500);                       // wait for a second

  // loopbackAFE();
}

/*
{OUT2B_P,OUT1B_P,OUT1A_P,OUT2A_P}
afe   3         1        4     2
fpga  3         2         1    0 

=--------------
FR      4
2       1 
3    
   
        DCO
--------------

=--------------
FR      1A
2A      1B
2B    
   
        DCO
--------------
  
*/



void loopbackAFE() {

  int freq = 10000;  //hz


  //write BEEF to a register
  // digitalWrite(AFE_CE_PIN, 0);
  // spi_write(AFE_MOSI_PIN, AFE_SCK_PIN, freq, MSBFIRST, SPI_MODE3, 24, 0x031100);
  // digitalWrite(AFE_CE_PIN, 1);

  // delay(5);


  // //write to enable reads
  // digitalWrite(AFE_CE_PIN, 0);
  // spi_write(AFE_MOSI_PIN, AFE_SCK_PIN, freq, MSBFIRST, SPI_MODE3, 24, 0x000002);
  // digitalWrite(AFE_CE_PIN, 1);

  // delay(5);


  // //read BEEF from the register
  // digitalWrite(AFE_CE_PIN, 0);
  // spi_write(AFE_MOSI_PIN, AFE_SCK_PIN, freq, MSBFIRST, SPI_MODE3, 24, 0x031100);
  // digitalWrite(AFE_CE_PIN, 1);
  


  // delay(5);


  // //write to enable writes
  // digitalWrite(AFE_CE_PIN, 0);
  // spi_write(AFE_MOSI_PIN, AFE_SCK_PIN, freq, MSBFIRST, SPI_MODE3, 24, 0x000000);
  // digitalWrite(AFE_CE_PIN, 1);

  //real config

  digitalWrite(AFE_CE_PIN, 0);
  spi_write(AFE_MOSI_PIN, AFE_SCK_PIN, freq, MSBFIRST, SPI_MODE3, 24, 0x000001);
  digitalWrite(AFE_CE_PIN, 1);

  delay(5);


  digitalWrite(AFE_CE_PIN, 0);
  spi_write(AFE_MOSI_PIN, AFE_SCK_PIN, freq, MSBFIRST, SPI_MODE3, 24, 0x040018);
  digitalWrite(AFE_CE_PIN, 1);

  delay(5);

  int channel_enable = 0b00000101; //1=on, 0=off

  // LNA Gain
  // 2 bits 
  // 00: 18 dB
  // 01: 24 dB
  // 10: 15 dB
  // 11: Reserved
  int lna_gain = 0b10; 
  
  // PGA Gain
  // 1 bit
  // 0:24 dB
  // 1:30 dB
  int pga_gain = 0b0;

  // Active Termination
  // 1 bit
  // 0: Disable
  // 1: Enable active termination
  int act_term = 0b0;


  // VCA Attenuation
  // 3 bits
  // 000: 0-dB attenuation
  // 001: 6-dB attenuation
  // N: About N * 6 dB attenuation
  int vca_attn = 0b000;

  // Test Pattern
  // 3 Bits
  // 000: Normal operation
  // 001: Sync
  // 010: De-skew
  // 011: Custom
  // 2[15:13] 0x2[15:13] 0 TEST_PATTERN_MODES 100:All 1's
  // 101: Toggle
  // 110: All 0's
  // 111: Ramp. Note: Reg.0x16 should be set as 1, i.e. demodulator is disabled.
  int test_pattern = 0b000;

  digitalWrite(AFE_CE_PIN, 0);
  spi_write(AFE_MOSI_PIN, AFE_SCK_PIN, freq, MSBFIRST, SPI_MODE3, 24, 0x0207F8 ^ (channel_enable << 3) | (test_pattern << 13));//E=ramp, 8=1s, LVDS shut down. Channel 1 analog 0x0207F0
                                                                                // Channel 8 Ramp 0x02E3F8
  digitalWrite(AFE_CE_PIN, 1);

  //LVDS shut down 10:3
  /*
  7F8 all channels

  1 2 3 4
  0 0 0 0   0x02E7F8
  1 0 0 0   0x02E7F0
  0 1 0 0   0x02E7E8
  1 1 0 0   0x02E7E0
  0 0 1 0   0x02E7D8
  1 0 1 0   0x02E7D0
  0 1 1 0   0x02E7C8
  1 1 1 0   0x02E7C0
  0 0 0 1   0x02E7B8
  1 0 0 1   0x02E7B0
  0 1 0 1   0x02E7A8
  1 1 0 1   0x02E7A0
  0 0 1 1   0x02E798
  1 0 1 1   0x02E790
  0 1 1 1   0x02E788
  1 1 1 1   0x02E780


  */
  delay(5);

  digitalWrite(AFE_CE_PIN, 0);
  spi_write(AFE_MOSI_PIN, AFE_SCK_PIN, freq, MSBFIRST, SPI_MODE3, 24, 0x0183FC ^ (channel_enable << 2)); //shut down ADCs. Channel 1 on: 0x0183F8. 1&3: 0x0183E8
                                                                                 //power down is bits [9:2]
                                                                                 //1&2 0x0183F0
                                                                                 //8 0x0181FC
  digitalWrite(AFE_CE_PIN, 1);

  delay(5);

  digitalWrite(AFE_CE_PIN, 0);
  spi_write(AFE_MOSI_PIN, AFE_SCK_PIN, freq, MSBFIRST, SPI_MODE3, 24, 0x3500FF ^ (channel_enable << 0)); //shut down LNAs. Channel 1 on: 0x3500FE 1&3: 0x3500FA
                                                                                 //power down is bits [7:0]
                                                                                 //1&2 0x3500FC
                                                                                 //8 0x35007F
  digitalWrite(AFE_CE_PIN, 1);

  delay(5);

  digitalWrite(AFE_CE_PIN, 0);
  spi_write(AFE_MOSI_PIN, AFE_SCK_PIN, freq, MSBFIRST, SPI_MODE3, 24, 0x030000);
  digitalWrite(AFE_CE_PIN, 1);

  delay(5);

  // AFE5812 only
  digitalWrite(AFE_CE_PIN, 0);
  spi_write(AFE_MOSI_PIN, AFE_SCK_PIN, freq, MSBFIRST, SPI_MODE3, 24, 0x160001); //turn off demodulator
  digitalWrite(AFE_CE_PIN, 1);

  delay(5);

  digitalWrite(AFE_CE_PIN, 0);
  spi_write(AFE_MOSI_PIN, AFE_SCK_PIN, freq, MSBFIRST, SPI_MODE3, 24, 0x340000 | (act_term << 8) | (lna_gain << 13)); //active termination 0x342100 vs not 0x342000
  digitalWrite(AFE_CE_PIN, 1);

  delay(5);

  digitalWrite(AFE_CE_PIN, 0);
  spi_write(AFE_MOSI_PIN, AFE_SCK_PIN, freq, MSBFIRST, SPI_MODE3, 24, 0x330008 | (pga_gain << 13)); //PGA gain 30 db: 0x332008, 24db: 0x330008
  digitalWrite(AFE_CE_PIN, 1);

  delay(5);

  digitalWrite(AFE_CE_PIN, 0);
  spi_write(AFE_MOSI_PIN, AFE_SCK_PIN, freq, MSBFIRST, SPI_MODE3, 24, 0x3B0088 | (vca_attn << 4)); //Attenuation, 0 db 0x3B0088, -30 db 0x3B00D8
  digitalWrite(AFE_CE_PIN, 1);

  delay(5);


}

//address goes from 0-3
void configureCDC7005() {

  // write each data word
  for (int i = 0; i < 4; i++) {
    // gain control of the SPI port
    // and configure settings
    SPI.beginTransaction(SPISettings(4000000, MSBFIRST, SPI_MODE0));
    // take the SS pin low to select the chip:
    digitalWrite(slaveSelectPin, LOW);
    //write each byte in the word
    for (int j = 3; j >= 0; j--) {
      SPI.transfer(words[i][j]);
    }
    // take the SS pin high to de-select the chip:
    digitalWrite(slaveSelectPin, HIGH);
    // release control of the SPI port
    SPI.endTransaction();
  }
}

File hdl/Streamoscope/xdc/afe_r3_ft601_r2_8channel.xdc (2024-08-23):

#pin ft_rxf A28;
#pin ft_txe A27;

#pin ft_data[0] B24;
#pin ft_data[1] B23;
#pin ft_data[2] B21;
#pin ft_data[3] B20;
#pin ft_data[4] B18;
#pin ft_data[5] B17;
#pin ft_data[6] B15;
#pin ft_data[7] B14;
#pin ft_data[8] B27;
#pin ft_data[9] B28;
#pin ft_data[10] B30;
#pin ft_data[11] B31;
#pin ft_data[12] B36;
#pin ft_data[13] B37;

#pin ft_data[14] A21;
#pin ft_data[15] A20;
#pin ft_be[0] A18;
#pin ft_be[1] A17;

#pin ft_rd A31;
#pin ft_wr A30;
#pin ft_oe B34;

#set_property PACKAGE_PIN L4 [get_ports LVDS_RX_P]
#set_property IOSTANDARD LVDS_25 [get_ports LVDS_RX_P]
#set_property PACKAGE_PIN M4 [get_ports LVDS_RX_N]
#set_property IOSTANDARD LVDS_25 [get_ports LVDS_RX_N]

#set_property PACKAGE_PIN P4 [get_ports LVDS_TX_P]
#set_property IOSTANDARD LVDS_25 [get_ports LVDS_TX_P]
#set_property PACKAGE_PIN P3 [get_ports LVDS_TX_N]
#set_property IOSTANDARD LVDS_25 [get_ports LVDS_TX_N]

#alchitry 100mhz clock
set_property PACKAGE_PIN N14 [get_ports CLK]
set_property IOSTANDARD LVCMOS25 [get_ports CLK]

#alchitry leds
set_property PACKAGE_PIN K13 [get_ports LED[0]]
set_property IOSTANDARD LVCMOS25 [get_ports LED[0]]
set_property PACKAGE_PIN K12 [get_ports LED[1]]
set_property IOSTANDARD LVCMOS25 [get_ports LED[1]]
set_property PACKAGE_PIN L14 [get_ports LED[2]]
set_property IOSTANDARD LVCMOS25 [get_ports LED[2]]
set_property PACKAGE_PIN L13 [get_ports LED[3]]
set_property IOSTANDARD LVCMOS25 [get_ports LED[3]]
set_property PACKAGE_PIN M16 [get_ports LED[4]]
set_property IOSTANDARD LVCMOS25 [get_ports LED[4]]
set_property PACKAGE_PIN M14 [get_ports LED[5]]
set_property IOSTANDARD LVCMOS25 [get_ports LED[5]]
set_property PACKAGE_PIN M12 [get_ports LED[6]]
set_property IOSTANDARD LVCMOS25 [get_ports LED[6]]
set_property PACKAGE_PIN N16 [get_ports LED[7]]
set_property IOSTANDARD LVCMOS25 [get_ports LED[7]]


# FT601 USB Signals

set_property PACKAGE_PIN N6 [get_ports USB_BE[0]]
set_property IOSTANDARD LVCMOS25 [get_ports USB_BE[0]]
#FT601 K1 : FT600 H1
set_property PACKAGE_PIN N9 [get_ports USB_BE[1]]
set_property IOSTANDARD LVCMOS25 [get_ports USB_BE[1]]
set_property PACKAGE_PIN P9 [get_ports USB_BE[2]]
set_property IOSTANDARD LVCMOS25 [get_ports USB_BE[2]]
set_property PACKAGE_PIN P8 [get_ports USB_BE[3]]
set_property IOSTANDARD LVCMOS25 [get_ports USB_BE[3]]

set_property PACKAGE_PIN P11 [get_ports USB_DATA[0]]
set_property IOSTANDARD LVCMOS25 [get_ports USB_DATA[0]]
set_property PACKAGE_PIN P10 [get_ports USB_DATA[1]]
set_property IOSTANDARD LVCMOS25 [get_ports USB_DATA[1]]
set_property PACKAGE_PIN N12 [get_ports USB_DATA[2]]
set_property IOSTANDARD LVCMOS25 [get_ports USB_DATA[2]]
set_property PACKAGE_PIN P13 [get_ports USB_DATA[3]]
set_property IOSTANDARD LVCMOS25 [get_ports USB_DATA[3]]
set_property PACKAGE_PIN N13 [get_ports USB_DATA[4]]
set_property IOSTANDARD LVCMOS25 [get_ports USB_DATA[4]]
set_property PACKAGE_PIN M1 [get_ports USB_DATA[5]]
set_property IOSTANDARD LVCMOS25 [get_ports USB_DATA[5]]
set_property PACKAGE_PIN M2 [get_ports USB_DATA[6]]
set_property IOSTANDARD LVCMOS25 [get_ports USB_DATA[6]]
set_property PACKAGE_PIN P1 [get_ports USB_DATA[7]]
set_property IOSTANDARD LVCMOS25 [get_ports USB_DATA[7]]
set_property PACKAGE_PIN N1 [get_ports USB_DATA[8]]
set_property IOSTANDARD LVCMOS25 [get_ports USB_DATA[8]]
set_property PACKAGE_PIN R1 [get_ports USB_DATA[9]]
set_property IOSTANDARD LVCMOS25 [get_ports USB_DATA[9]]
set_property PACKAGE_PIN R2 [get_ports USB_DATA[10]]
set_property IOSTANDARD LVCMOS25 [get_ports USB_DATA[10]]
set_property PACKAGE_PIN T2 [get_ports USB_DATA[11]]
set_property IOSTANDARD LVCMOS25 [get_ports USB_DATA[11]]
# B2 not E2!!!! The alchitry footprint has a mistake
set_property PACKAGE_PIN R3 [get_ports USB_DATA[12]] 
set_property IOSTANDARD LVCMOS25 [get_ports USB_DATA[12]]
set_property PACKAGE_PIN T3 [get_ports USB_DATA[13]]
set_property IOSTANDARD LVCMOS25 [get_ports USB_DATA[13]]
set_property PACKAGE_PIN T4 [get_ports USB_DATA[14]]
set_property IOSTANDARD LVCMOS25 [get_ports USB_DATA[14]]
set_property PACKAGE_PIN T13 [get_ports USB_DATA[15]]
set_property IOSTANDARD LVCMOS25 [get_ports USB_DATA[15]]
set_property PACKAGE_PIN R13 [get_ports USB_DATA[16]]
set_property IOSTANDARD LVCMOS25 [get_ports USB_DATA[16]]
set_property PACKAGE_PIN T12 [get_ports USB_DATA[17]]
set_property IOSTANDARD LVCMOS25 [get_ports USB_DATA[17]]
set_property PACKAGE_PIN P5 [get_ports USB_DATA[18]]
set_property IOSTANDARD LVCMOS25 [get_ports USB_DATA[18]]
set_property PACKAGE_PIN R12 [get_ports USB_DATA[19]]
set_property IOSTANDARD LVCMOS25 [get_ports USB_DATA[19]]
set_property PACKAGE_PIN R11 [get_ports USB_DATA[20]]
set_property IOSTANDARD LVCMOS25 [get_ports USB_DATA[20]]
set_property PACKAGE_PIN R10 [get_ports USB_DATA[21]]
set_property IOSTANDARD LVCMOS25 [get_ports USB_DATA[21]]
set_property PACKAGE_PIN L5 [get_ports USB_DATA[22]]
set_property IOSTANDARD LVCMOS25 [get_ports USB_DATA[22]]
set_property PACKAGE_PIN M5 [get_ports USB_DATA[23]]
set_property IOSTANDARD LVCMOS25 [get_ports USB_DATA[23]]
set_property PACKAGE_PIN N4 [get_ports USB_DATA[24]]
set_property IOSTANDARD LVCMOS25 [get_ports USB_DATA[24]]
set_property PACKAGE_PIN L4 [get_ports USB_DATA[25]]
set_property IOSTANDARD LVCMOS25 [get_ports USB_DATA[25]]
set_property PACKAGE_PIN M4 [get_ports USB_DATA[26]]
set_property IOSTANDARD LVCMOS25 [get_ports USB_DATA[26]]
set_property PACKAGE_PIN P4 [get_ports USB_DATA[27]]
set_property IOSTANDARD LVCMOS25 [get_ports USB_DATA[27]]
set_property PACKAGE_PIN P3 [get_ports USB_DATA[28]]
set_property IOSTANDARD LVCMOS25 [get_ports USB_DATA[28]]
set_property PACKAGE_PIN N3 [get_ports USB_DATA[29]]
set_property IOSTANDARD LVCMOS25 [get_ports USB_DATA[29]]
set_property PACKAGE_PIN N2 [get_ports USB_DATA[30]]
set_property IOSTANDARD LVCMOS25 [get_ports USB_DATA[30]]
set_property PACKAGE_PIN M6 [get_ports USB_DATA[31]]
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

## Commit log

2024-08-23 added zadig image and teensy code
2024-08-23 teensy section of readme
2024-08-23 board files
    [afe_5812.kicad_sch, analog_input.kicad_sch, design_1.kicad_pcb, design_1.kicad_sch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]
